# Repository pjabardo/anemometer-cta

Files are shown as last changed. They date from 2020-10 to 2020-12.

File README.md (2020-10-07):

# Project of a thermistor based constant temperature anemometer

This repository contains files related to a constant temperature anemometer that uses a self heated NTC thermistor as a sensing element.

## Thermal anemometer

An anemometer is a device that measures fluid speed, in particular air. A thermal anemometer uses heat transfer from a heated element to estimate the velocity of the fluid. There are several ways to build a thermal anemometer but the most common is the use of a self heated resistor whose resistance varies with temperature.

As a side note, a few years ago, José Pucci Caly, a professor at Mackenzie University in São Paulo/Brazil developed with a couple of students a very simple anemometer: the external temperature of the bulb from an incandescent light bulb was calibrated against wind speed. It worked. How well? I don't remember...

There are several ways that a self heated resistor can be used as the two mosto common aproaches are:

 * Constant temperature
 * Constant current

In this project we use the constant temperature approach.

## CTA - Constant temperature anemometer

The basic idea behind the constant temperature anemometer (CTA) is that an electric current passing through a resistor will heat the resistor. The temperature of the resistor is the result of the heat transfer to the fluid flowing around it.

Now suppose that for a given fluid velocity the temperature of the resistor is Tw. If the velocity then increases a tiny bit, Tw should drop a little bit. This drop in temperature corresponds to a change in resistance (when the resistance depends on the temperature). This change in resistance can be picked up and the current flowing through the resistor is changed accordingly.

The figure below shows the basic idea behind the anemometer. In this figure, Rw is the sensor. An imbalance of the Wheatsone bridge will cause a change of the current on the feedback loop. While this basic layout explains in general terms what is being done, it doesn't work. For one, most op amps can not provide sufficient current to the bridge. But there are other issues with this simple scheme.

Basic feedback circuit

This project uses an NTC thermistor (<https://en.wikipedia.org/wiki/Thermistor>) as a sensing element. In this case, an increase in temperature results in a decrease of resistance. This change can be drastic. For instance for a thermistor with a resistance of 5k at 25oC, at 180oC, the resistance can be 100 Ohms.

## Understanding the circuit

If the flow spead increases, the temperature will decrease and therefore the thermistor's resistance wqill increase and the voltage just before the sensor will increase and that will increase the output from the op amp so that it restores balance. To handle larger currents, the output of the op amp is connected to the base of an NPN transistor.

Even with the transistor in place, the circuit will not work. How does it start? When the power is turned on, there is no current on the bridge and therefore no imbalance and the base current is zero. So the circuit stays off indefinitely.

One possible solution is to nudge the + input of the op amp by connecting it to input voltage using a large resistor. This will work but now we have a problem: the operating point of the circuit will depend on the input voltage. This is not good. The figure below shows the basic circuit used:

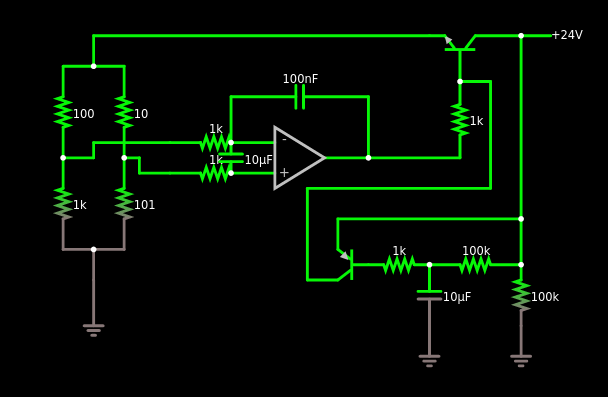
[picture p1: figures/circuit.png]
Circuit of the CTA


This figure was generated from the text file  `cta-circuit.txt` using the online Falstad circuit simulator (<https://www.falstad.com/circuit/circuitjs.html>). Go to the previous link, select File -> Import from text and copy and paste the contents of the `cta-circuit.txt` file.

This is the completed circuit. The sub-circuit on the lower right hand side of the circuit basically unbalances the + input of op amp during power up so that the circuit is started. When the 10uF capacitor is charged, the PNP transistor is switched off and this branch of the circuit plays no role anymore.

There is now an input filter at the op amp. Without the feedback capacitor, once the bridge reached equilibrium, the current would be cutoff. The 100nF capacitor works as a integral controller.

The output of the anemometer is the voltage feeding the sensor. This output is fed to a voltage follower and then to a voltage divider to lower the voltage to levels adequate to an analog to digital converter and then there is another voltage follower to isolate the output.

This circuit uses 3 op amps and the LM324 quad 
## KiCad schematics

On the `kicad` folder is the KiCad project of the circuit.

## The finished board

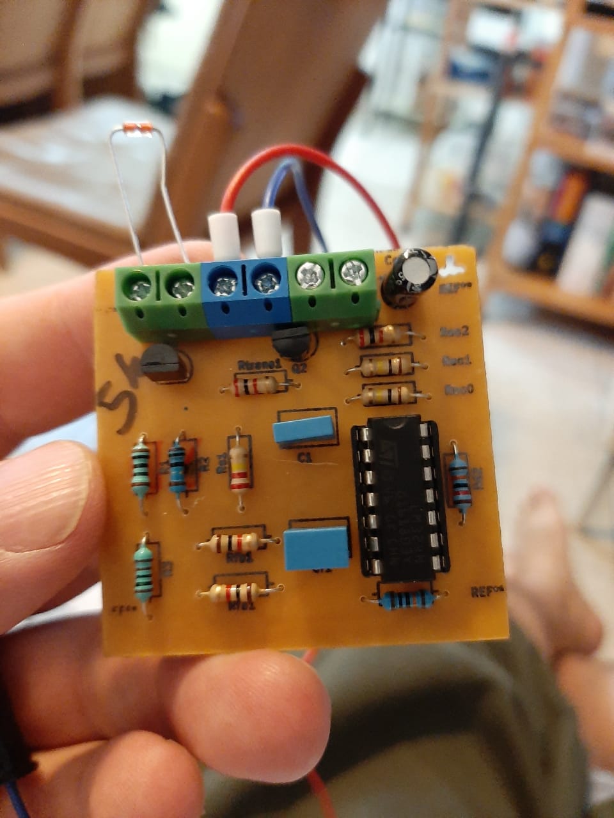
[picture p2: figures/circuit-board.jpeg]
Circuit of the CTA


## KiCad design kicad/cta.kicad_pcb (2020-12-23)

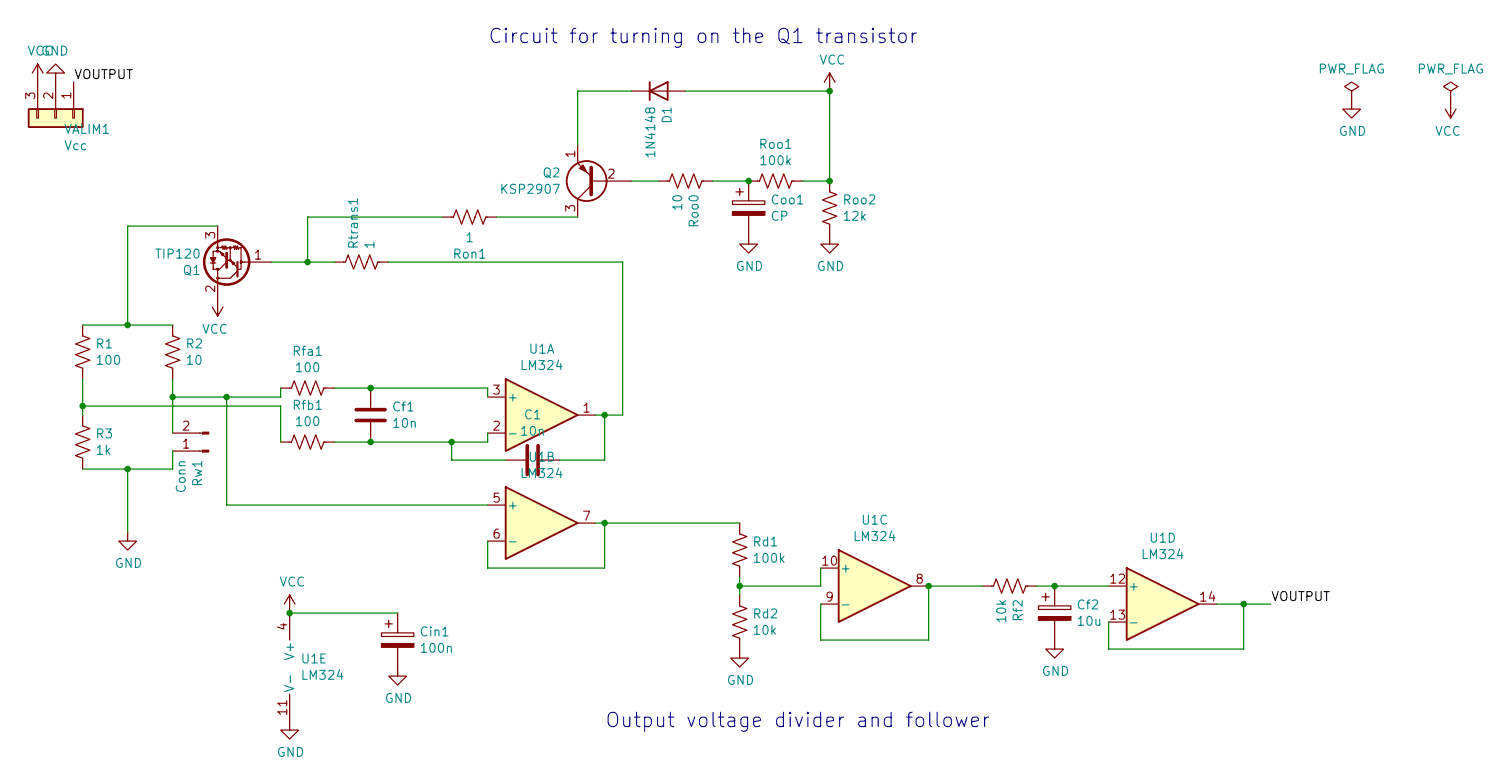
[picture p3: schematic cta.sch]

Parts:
C1: 10n; C_Rect_L7.2mm_W4.5mm_P5.00mm_FKS2_FKP2_MKS2_MKP2
Cf1: 10n; C_Rect_L7.2mm_W4.5mm_P5.00mm_FKS2_FKP2_MKS2_MKP2
Cf2: 10u; CP_Radial_D5.0mm_P2.50mm
Cin1: 100n; CP_Radial_D4.0mm_P2.00mm
Coo1: CP; CP_Radial_D5.0mm_P2.50mm
D1: 1N4148; D_DO-35_SOD27_P7.62mm_Horizontal
Q1: TIP120; TO-220-3_Vertical
Q2: KSP2907; TO-92_Inline_Wide
R1: 100; R_Axial_DIN0207_L6.3mm_D2.5mm_P10.16mm_Horizontal
R2: 10; R_Axial_Power_L20.0mm_W6.4mm_P22.40mm
R3: 1k; R_Axial_DIN0207_L6.3mm_D2.5mm_P10.16mm_Horizontal
Rd1: 100k; R_Axial_DIN0207_L6.3mm_D2.5mm_P10.16mm_Horizontal
Rd2: 10k; R_Axial_DIN0207_L6.3mm_D2.5mm_P10.16mm_Horizontal
Rf2: 10k; R_Axial_DIN0207_L6.3mm_D2.5mm_P10.16mm_Horizontal
Rfa1: 100; R_Axial_DIN0207_L6.3mm_D2.5mm_P10.16mm_Horizontal
Rfb1: 100; R_Axial_DIN0207_L6.3mm_D2.5mm_P10.16mm_Horizontal
Ron1: 1; R_Axial_DIN0207_L6.3mm_D2.5mm_P10.16mm_Horizontal
Roo0: 10; R_Axial_DIN0207_L6.3mm_D2.5mm_P10.16mm_Horizontal
Roo1: 100k; R_Axial_DIN0207_L6.3mm_D2.5mm_P10.16mm_Horizontal
Roo2: 12k; R_Axial_DIN0207_L6.3mm_D2.5mm_P10.16mm_Horizontal
Rtrans1: 1; R_Axial_DIN0207_L6.3mm_D2.5mm_P10.16mm_Horizontal
Rw1: Conn; TerminalBlock_bornier-2_P5.08mm
U1: LM324; DIP-14_W7.62mm_LongPads
VALIM1: Vcc; TerminalBlock_bornier-3_P5.08mm

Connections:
/VOUTPUT: U1.13 (-), U1.14, VALIM1.1
GND: Cf2.2, Cin1.2, Coo1.2, R3.2, Rd2.1, Roo2.2, Rw1.1, U1.11 (V-), VALIM1.2
unnamed: C1.1, Rtrans1.2, U1.1
unnamed: C1.2, Cf1.2, Rfb1.1, U1.2 (-)
unnamed: Cf1.1, Rfa1.1, U1.3 (+)
unnamed: Cf2.1, Rf2.1, U1.12 (+)
unnamed: Coo1.1, Roo0.1, Roo1.2
unnamed: D1.1 (K), Q2.1 (E)
unnamed: Q1.1 (B), Ron1.1, Rtrans1.1
unnamed: Q1.3 (E), R1.1, R2.1
unnamed: Q2.2 (B), Roo0.2
unnamed: Q2.3 (C), Ron1.2
unnamed: R1.2, R3.1, Rfb1.2
unnamed: R2.2, Rfa1.2, Rw1.2, U1.5 (+)
unnamed: Rd1.1, U1.6 (-), U1.7
unnamed: Rd1.2, Rd2.2, U1.10 (+)
unnamed: Rf2.2, U1.8, U1.9 (-)
VCC: Cin1.1, D1.2 (A), Q1.2 (C), Roo1.1, Roo2.1, U1.4 (V+), VALIM1.3

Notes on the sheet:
Circuit for turning on the Q1 transistor
Output voltage divider and follower

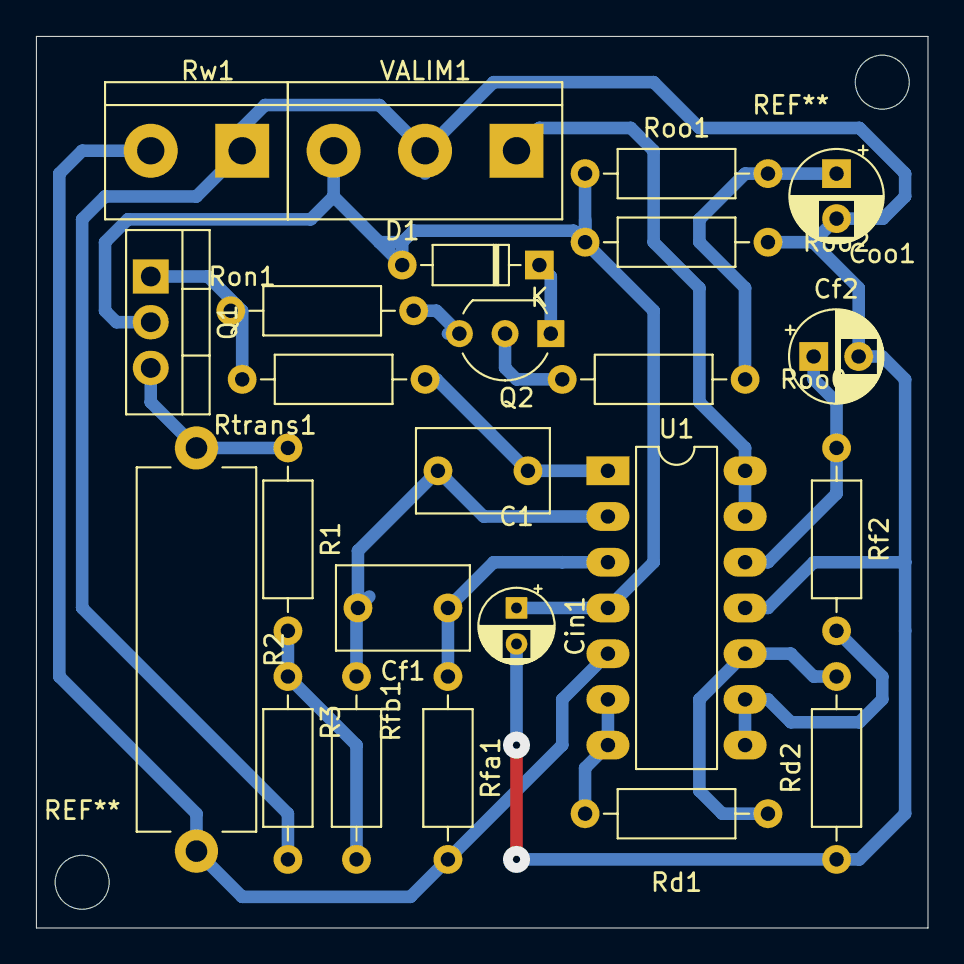
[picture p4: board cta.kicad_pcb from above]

Board: 2 copper layers, 49.5 x 49.5 mm, 24 parts (0 on the bottom side), 18 nets.

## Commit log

2020-10-06 Initial commit of the anemometer-cta project.
    This project is an attempt to develop a constant temperature anemometer.
    This project uses KiCad.
    [cta.kicad_pcb, cta.sch]
2020-10-07 Working on the README.md file
    Explaining how the anemometer works.
    [cta.kicad_pcb, cta.sch]
2020-10-07 The README.md file explains the circuit
2020-10-21 Modified the warmup subcircuit
    To initialize the circuit, a subcircuit was used that on powerup would
    temporarily add voltage to the + leg of the op amp. Now this circuit adds
    this voltage directly to the base of Q1. With this I could also remove
    the resistor conecting both cricuits (Rs1).
    I also decreased the fill zones tolerances and most of the board is now
    filled.
    [cta.kicad_pcb, cta.sch]
2020-10-21 Updated the circuit code for the falstad circuit simulator.
    And the corresponding figure on the README.md file.
2020-10-25 Fixed a few things but there are several issues that I should fix
    It is very difficult to solder the transistors. I will change the footprint to To-92L wide.
    Another issue is that the board, as designed is 2 in by 2 in. But the copper
    boards that I usually find are 50 mm. I should set edge cut to that measure.
    [cta.kicad_pcb]
2020-10-25 Improved board layout and allowed for a power resistor.
    [cta.kicad_pcb, cta.sch]
2020-10-25 Removed a terminal block and increased the power termninal block to 3
    The circuit uses the same ground for power and signal. So I removed the signal terminal block and added another terminal to the power terminal block
    [cta.kicad_pcb, cta.sch]
2020-10-25 Forgot to add mounting holes
    Now I have to test this new board
    [cta.kicad_pcb]
2020-10-29 Set new values for components
    One of the things I noticed with the circuit is an asymmetry when increasing wind speed vs decreasing. When increasing, the response is fast. But when decreasing it is very low.
    This is to be expected: the electronics respond much faster than the cooling: the maximum colling rate happens when there is no current and therefore heat transfer within the thermistor is the slow p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
    To make response more symmetric, I increased the the resistors at the op amp input from 1k to 47k. This introduced a new problem: the capacitor would not charge fast enough for the initial charge sub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
    [cta.kicad_pcb, cta.sch]
2020-10-29 Replaced transistor KSP2222A for BC517
    The BC517 is a darlington transistor and the response of the anemometer is much faster (when increasing wind speed). Why would I care about that if I went to all the trouble to make the response more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
    It really depends on the objective. If I want to measure the mean speed in a turbulent flow, using the more symmetric response is better. But If I want to estimate wind gusts, the faster response tim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
    [cta.kicad_pcb, cta.sch]
2020-10-30 I found out the trouble: too much power dissipated on the tranistor
    During normal operation, the current is low and therefore the voltage at the top of the bridge is low and the transistor needs to reduce a lot of voltage and dissipate a lot of heat. After normal ope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
    I see 2 solutions:
    1. Replace the transistor
    2. Modify the resistors
    I think I will do #2 anyway and do #2.
    [cta.kicad_pcb, cta.sch]
2020-10-30 Replaced the transistor from BC517 to TIP120 and resistors on the bridge
    The resistors on the top of the bridge now have the same value as on the bottom of the bridge. This decreased the power dissipated in the transistor.
    The new transistor can also include a heat sink dependeing on application. The setup is working on the protoboard. I has been working for the last hour, voltage input can be decreased to 15V and the 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
    [cta.kicad_pcb, cta.sch]
2020-11-02 Cleaned up the schematics
    The circuit is much clearer! I have tested the circuit 24 hours and it is working. Now I have to test it on a wind tunnel and checkout how well it operates.
    [cta.kicad_pcb, cta.sch]
2020-11-04 Used the last op amp to implement an active low pass output filter
    I think this is the best strategy to get a symmetric behavior when heating or cooling. Just get a time constant larger than the corresponding cooling time constant.
    [cta.kicad_pcb, cta.sch]
2020-12-13 The circuit was not working with low noise, low offset op amp
    I removed the input filter and the cicrcuit works with precision op amps. Stilll need to test the circuit exhaustively.
    [cta.kicad_pcb, cta.sch]
2020-12-23 Added a decoupling capacitor to op amp and improved layout
    I don't know if this will help but it may reduce noise and improve performance when voltage input is noisy.
    [cta.kicad_pcb, cta.sch]
